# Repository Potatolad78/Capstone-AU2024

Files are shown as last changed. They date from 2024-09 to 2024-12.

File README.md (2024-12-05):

## Table of Contents
1. [Project Overview](#project-overview)
    - [What is pH and how is it important to oceanography?](#what-is-ph-and-how-is-it-important-to-oceanography)
    - [What relevance does this have to computer science?](#what-relevance-does-this-have-to-computer-science)
    - [What use might this project have in high school curriculum?](#what-use-might-this-project-have-in-high-school-curriculum)
2. [Why use this as a project?](#why-use-this-as-a-project)
3. [What will I need?](#what-will-i-need)
    - [Deployment Materials](#deployment-materials)
    - [Perfboard or Breadboard?](#perfboard-or-breadboard)
    - [Wires or Jumpers?](#wires-or-jumpers)
4. [How do I solder?](#how-do-i-solder)
5. [What IDE should I use?](#what-ide-should-i-use)
6. [First Steps](#first-steps)
7. [Soldering Your PerfBoard](#soldering-your-perfboard)
    - [Soldering the Pico](#soldering-the-pico)
    - [Soldering the Power Buses](#soldering-the-power-buses)
    - [Soldering Out Pins](#soldering-out-pins)
8. [Printing Your Parts](#printing-your-parts)
9. [Putting Things Together](#putting-things-together)
    - [Deployment](#deployment)
    - [Connecting Wires](#connecting-wires)
10. [Calibrating the Machine](#calibrating-the-machine)
11. [Troubleshooting](#troubleshooting)
    - [Compartmentalizing](#compartmentalizing)
    - [Taking a Break](#taking-a-break)

## Project Overview
This project, developed by Drew Rigby as a capstone for the Applied Computing major at the University of Washington Bothell, integrates computer science concepts with oceanography, reflecting the intersection of my major and minor. The objective was to design and build an automated pH sensor capable of sampling water and providing accurate pH measurements.

An important goal of this project is to make it accessible for high school students, even those with little to no background in oceanography, coding, or electrical engineering. To achieve this, the project includes a comprehensive manual that provides detailed, step-by-step instructions, ensuring that anyone can build, use, and understand the sensor regardless of prior experience. This focus on accessibility aims to inspire students and foster interest in STEM and environmental science.

### What is pH and how is it important to oceanography?
pH measures the acidity or alkalinity of a substance. This project focuses specifically on the pH of water, a critical parameter in oceanography. One of the most pressing issues in this field is ocean acidification, a phenomenon where the ocean's pH decreases, becoming more acidic.

Ocean acidification has far-reaching consequences for marine ecosystems. For example, reduced levels of calcium carbonate in acidic waters hinder marine organisms, such as mollusks and corals, from forming their shells and skeletons. This disruption cascades through the food chain, potentially impacting human industries and livelihoods. Monitoring pH levels in vulnerable areas can provide valuable insights into the causes and effects of ocean acidification, aiding research and mitigation efforts.

### What relevance does this have to computer science?
This project leverages computer science principles through the use of a Raspberry Pi Pico and embedded systems programming to bring the sensor to life. I applied my expertise to develop a library that simplifies interaction with the sensor, enabling users to perform essential tasks with straightforward functions while maintaining flexibility for advanced customization.

For example, users can easily explore different configurations, such as testing alternative calibration curves using purple instead of green color indicators, by utilizing specific functions provided in the library. This design empowers users to adapt the sensor's functionality to their needs, balancing ease of use with the ability to conduct more complex experiments.

### What Use Might This Project Have in High School Curriculum?
This project is an excellent tool for high school science curriculum, offering students hands-on experience with STEM concepts while encouraging critical thinking and hypothesis testing. The sensor’s flexibility, made possible through its programmable library, allows students to explore a variety of experiments and customize its functionality to suit their needs. For instance, the library includes functions that enable users to adjust calibration curves or test alternative parameters, such as using different color indicators for measurements.

This adaptability provides students with the opportunity to investigate real-world scientific questions, such as how environmental factors like temperature or salinity influence pH levels. By designing and conducting their experiments, students can better understand the scientific method and the role of data in validating hypotheses. The comprehensive manual ensures accessibility, making the sensor usable even by those with little to no prior knowledge of oceanography, coding, or electrical engineering. This combination of flexibility, ease of use, and educational potential makes the project an invaluable resource for inspiring curiosity and fostering skills in STEM fields.

## Why use this as a project?
This project offers a unique blend of accessibility, adaptability, and real-world relevance, making it an excellent choice for educators, students, and STEM enthusiasts alike.

Hands-On Learning: The sensor provides a tangible way to explore STEM concepts, bridging the gap between theory and practice. Students can learn about coding, embedded systems, and environmental science while working on a meaningful, real-world application.

Flexibility: The custom library included with the project allows for significant experimentation and customization. Users can test various calibration methods, explore alternative parameters, and tailor the sensor’s functionality to align with specific learning objectives or experiments.

Accessibility: Designed with ease of use in mind, this project is accessible to individuals with minimal background knowledge in coding, oceanography, or electrical engineering. The detailed manual ensures that even beginners can confidently assemble, program, and operate the sensor.

Real-World Relevance: By focusing on issues like ocean acidification, this project highlights the critical role of technology in addressing environmental challenges. It inspires students to think about how STEM disciplines can be applied to solve pressing global problems.

Incorporating this project into a classroom or individual learning plan can spark curiosity, enhance problem-solving skills, and encourage exploration in the interconnected fields of science and technology.

## What will I need?

|ITEM|QUANTITY|PRICE|
|---|---|---|
|[Raspberry Pi Pico](https://www.adafruit.com/product/5525)|1|$5|
|[Submersible 3V DV Water Pump](https://www.adafruit.com/product/4547)|1|$2.95|
|[Adafruit TSL2561*](https://www.voc-electronics.com/a-37456119/sensors-breakout-kits/adafruit-tsl2561-digital-luminosity-lux-light-sensor-breakout/#description)|1|$7.31|
|[Common Cathode RGB Light](https://www.sparkfun.com/products/105)|1|$2.25|
|[Phenol Red pH Indicator Dye](https://www.poolweb.com/products/taylor-ph-indicator-solution-3-4-oz-dropper-bottle-r-0014-a)|1|$3.38|
|[GT-U7 GPS](https://www.amazon.com/Navigation-Satellite-Compatible-Microcontroller-Geekstory/dp/B07PRGBLX7)|1|$14.99|
|[Cuvette 1.5ML *This link only sells by the 10s*](https://www.amazon.com/Standard-Disposable-Professional-Transparent-Spectrophotometers/dp/B07VGDLMMH/ref=sr_1_3?c=ts&dib=eyJ2IjoiMSJ9.Wdu-PneNgzy9HWgzqQpF4NBLH8vNxU3TnJP97jJI6K5CkgJXkyv-UAtbcqg3fmO8-xdRdEMT4H2ownpaVPMMaHXzsNkF2tbxrW2HuE7zxEcOtA-MBHBYkHV6HmPOE7fLuzGbI9rZSdy10q5kvpcnMFaT6kUqf7-DJbqa2snUjLDDArWAbArXT2QCQDNtBNRAVqzQem_6vUD536fPMKD2lA25uliqrV63WyjNQt6MhQQZa2gJIJN3Nr4TtDbrs_wtAlUK7JVekIs8ODg29hQC5DgXq_pKflS9gyPv6p5u7JI.71dC1E2u98ecs3xq6WpQIMiJ2LN3HRsqwCd--ipGPMc&dib_tag=se&keywords=Lab+Cuvettes&qid=1731213259&s=industrial&sr=1-3&ts_id=318063011)|1|$11.89|
|[20ML Syringe](https://aaprintsupplyco.com/products/neo-sy?variant=32983529488468&currency=USD&utm_medium=product_sync&utm_source=google&utm_content=sag_organic&utm_campaign=sag_organic&srsltid=AfmBOoqIWNiGqBFyY0_SuPJI8O2K_qD1SE5h-Gxxlw2TRUkzQtm_g3tpRyg)|1|$2|
|[Plastic Water Reservoir of your choosing](https://www.berlinpackaging.com/3600b03-2-oz-natural-hdpe-plastic-wide-mouth-packer-bottles-white-screw-top-cap/?utm_source=google&utm_medium=cpc&utm_campaign=PMax%3A%20%28ROI%29%20Shopping%20-%20Smart%20-%20Bottles%20-%20HDPE&utm_id=21016660230&utm_content=&utm_term=&gad_source=1&gclid=CjwKCAjw9cCyBhBzEiwAJTUWNQKtTxFOMuFaX5nl7jv3UimzFBc7M9naBo_MlGrCpJRQH1XFCfGRXBoCqS4QAvD_BwE)|1|$0.38|
|[Peristaltic Pump](https://www.adafruit.com/product/1150)|1|$24.95|
|[Relay](https://www.elecbee.com/en-29076-3V-1-Channl-Relay-Isolated-Drive-Control-Module-High-Level-Driver-Board)|3|$7.99|
|[Tubing](https://www.adafruit.com/product/4545)|2|$1.50|
|[Valve](https://www.amazon.com/SNS-Electric-Solenoid-Normally-Closed/dp/B0D4QN114D)|1|$15.69|
|[Adaptors](https://www.homedepot.com/p/Everbilt-1-4-in-Barb-x-1-4-in-MIP-Brass-Adapter-Fitting-800119/300096726?source=shoppingads&locale=en-US)|2|$4.45|
|Total||$116.62|

\* *They no longer make these sensors but this is all I had access to. In theory any sensor should work you would just need to change the library*
### Deployment Materials
You as the user will have to choose how you would like to deploy the sensor. I have the sensor mounted onto a boogie board with pool noodles attached as that provide flotation for sensor. I will include those materials listed here however
it is important to think of your use case for the sensor and if you will need sturdier materials or if you don't plan to deploy it on water at all instead from a dock.
|ITEM|QUANTITY|PRICE|
|---|---|---|
|[Boogie Board](https://www.dickssportinggoods.com/p/dbx-33-inbodyboard-19dbxudbx33bdybrdsbb/19dbxudbx33bdybrdsbb?sku=25341944&srsltid=AfmBOoplDu2-M7iMlmrVefRNFGweKAaN4pFO5CtZ6sZXx5XDULClXj2LsxM)|1|$14.99|
|[Pool Noodle](https://www.amazon.com/Swimming-Floating-Projects-Exercise-Accessories/dp/B0D5D16BLV?th=1)|2|$0.98|
|[Water Proof Casing](https://www.amazon.com/Waterproof-Plastic-Electronic-Junction-Enclosure/dp/B07M5SZNR9/ref=asc_df_B07M5SZNR9/?tag=hyprod-20&linkCode=df0&hvadid=693308318554&hvpos=&hvnetw=g&hvrand=13402671431230684644&hvpone=&hvptwo=&hvqmt=&hvdev=c&hvdvcmdl=&hvlocint=&hvlocphy=9033316&hvtargid=pla-615797795038&psc=1&mcid=7bd63229ef183828938a82ddd5446444&gad_source=1)|1|$9.49|
|[Cable Gland](https://www.adafruit.com/product/762)|2|$1.95|
|[Ruler](https://www.amazon.com/Mr-Stainless-Centimeters-Drawing-Measuring/dp/B07ZS4JSQP/ref=sxin_17_pa_sp_search_thematic-asin_sspa?content-id=amzn1.sym.04f61faa-8c24-439e-ba3b-8f0078642c9d%3Aamzn1.sym.04f61faa-8c24-439e-ba3b-8f0078642c9d&cv_ct_cx=12+inch+ruler+with+3+holes&keywords=12+inch+ruler+with+3+holes&pd_rd_i=B07ZS4JSQP&pd_rd_r=5daf147d-a691-4b7d-ab83-7f7bf00ba648&pd_rd_w=YHUGZ&pd_rd_wg=niOl4&pf_rd_p=04f61faa-8c24-439e-ba3b-8f0078642c9d&pf_rd_r=GV3FFFXFFZQZWE572363&qid=1733296388&sbo=RZvfv%2F%2FHxDF%2BO5021pAnSA%3D%3D&sr=1-1-baa1f287-65d3-41a3-a655-8bbba0531537-spons&sp_csd=d2lkZ2V0TmFtZT1zcF9zZWFyY2hfdGhlbWF0aWM&psc=1)|1|$5.99|
|[Zip Ties](https://www.amazon.com/Hmrope-Premium-Plastic-Strength-Self-Locking/dp/B07TG9VMWY?source=ps-sl-shoppingads-lpcontext&ref_=fplfs&psc=1&smid=A66IX15EHOXVO)|1|$3.99|
|Total||$39.34|

This does not include perfboards, wires, wiring tools, solder, soldering tools, or resistors. Those can be found below if you do not have them otherwise please skip past to the [Soldering Your Perfboard](#soldering-your-perfboard) section
This also does not include adhesive, I would recommend getting yourself some kind of strong sealant for creating the seal around the bottom of the cuvette and the valve however you could in theory use hot glue if you're good enough with it.
### Perfboard or Breadboard?
Perfboards are used when you are creating electrical circuits and would like a stable connection that doesn't require having jumper cables. This
does require soldering for connection of pins which can be dangerous if unsupervised. This also allows for less errors as things are easier to 
break. If you are going with perfboards I recommend a breadboard layout as there are the easiest to use as they have power buses(See Vocabulary)
built in. If you are going to use perfboards I would recommend using a bread board to make sure that you have a good understanding of the 
electronics before soldering things into place.


You can find a good perfboard [here](https://www.adafruit.com/product/1609) for $4.50

Breadboards on the other hand are less permanent but can have issues with pins not touching metal properly and are often seen as temporary solutions.
As said above in the perfboard section one should at least use a breadboard to plan out their circuit so one could save money by only using breadboards.


You can find a good breadboard [here](https://www.mouser.com/ProductDetail/SparkFun/PRT-12002?qs=WyAARYrbSnYNJEbsmDuXsA%3D%3D&mgh=1&srsltid=AfmBOopsiO3PD5JWbhyFv99flrAnsKZhypC7DzSwbdvFXANliHVx4DNLneM) for $4.95

### Wires or Jumpers?
Choosing between buying wires or jumpers is very difficult. If possible one should buy both as it allows for modularity when creating the ciruits however
if you can only afford one option then there are many things to consider.

#### What tools do I have acccess too?
If you have access to no tools and are trying to do this project without using any you are going to have a difficult time. If you are still going to try to
replicate the project without tools then you are going to want to go with jumpers as you wont have to wory as much about shortening them to the size that 
you need. However you will have to at least have access to solder for this project as not every module on the project has headers and to use jumpers you will
need to solder on headers. If you have access to things like wire cutters and wire strippers then normal wire should work perfectly. This will allow you to 
have more modularity and wires also just feel more professional. It also helps if you have solder sleeves and a heat gun as it allows for less precision when
soldering as for difficult things you can use said solder sleeves instead.

### How do I solder?
Soldering is a skill in its own right that is very difficult to master. For this project you should allocate a week or more to making sure that your skills 
are properly up to par with solder before permanently setting things into place. I recommend starting with watching this video:
<a href="http://www.youtube.com/watch?feature=player_embedded&v=rK38rpUy568
" target="_blank">IMAGE ALT TEXT HERE</a>

### What IDE should I use?
Before we get there it is important that you install the proper packages for python and install python itself. Installing python can be done [here](https://www.python.org/downloads/)

When python is done installing then you should also be able to run these commands in your terminalto get the needed libraries installed.

```console
pip install pyserial pandas matplotlib
```

You should install [Thonny](https://thonny.org/) as it will detect when you connect your pico to the system and on the bottom left you should be able to click
the com that your pico connects to and be able to edit code on said pico. To test this you should install the library directory and the main.py from the repo
onto the pico. Do this by going into Thonny, detecting your device and making sure that you have the device open it should look like this:



Highlight the files that you would like to move into the pico and then right click under the rapsbery pi pico section. It should say intall to and then have a directory
or an empty signature. Do that and see if those files are now in the pico section, if they are you succeeded in downloading those files onto your pico. Try also
creating a file on the pico, right click under the raspberry pi pico section and then click create file. Name said file test.py, this should open the file on 
the IDE. Go ahead and write:

```python
print("Hello World")
```

Then click crtl s and save the file. You should see the file appear on the bottom left side of your screen as test.py. You can now run your file using the green check mark in
the top left. Keep this file as when I have code written you can use this file to copy and paste said code into to make sure your components are working correctly

## First Steps
Going forward I am going to assume that you are going to be working with proper tools, wire, perfboards, and will be soldering. I am also going to assume that
you 3D printed the parts that are required in the project. If you do not then you will have to go off from the instructions. If you have questions you can email
me at the email phsensorguide@gmail.com.

## Soldering Your PerfBoard
### Soldering The Pico
When soldering your perfboard it is very important to try and avoid errors as these sre semi permanent. 
Raspberry Pi Pico Pinout
[Link to Pinout](https://microcontrollerslab.com/raspberry-pi-pico-pinout-features-programming-peripherals/)
I personally recommend that you dtart by soldering female header pins into the perfboard. The pico is 20 pins long so you will need a long enough strip of pins.
If you have a strip that us longer then you can use wire cutters to cut it down to size. Try and solder in a diagonal pattern, soldering one corner then another.
Remember that you should also be soldering the UNDERSIDE of the board and not the top. This along with a stabilization method(Tape the item into place in the front side) 
should help keep the female headers straight so you can slot the pico in flush.
The following picture is an example of pins soldered onto a board:
Pins on Perf
The following picture is an example of a pico slotted into header pins. (Note your female pins should be soldered onto the board not the pico)
Flush Pico

Once you have completed that you have successfully done the first step, congratulations! Next we will solder the power busses.

### Soldering The Power Buses
You should have space for two power busses on your perfboard. Assuming that you bought the perfboard I recommend then the two strips on the side are dedicated busses.
If you did not buy that board then you will have to solder your connections(Please note I will not be covering bridging connections and I recommend watching a video 
on it). You will see on your perfboard that there is a red positive side for the bus and a blue negative side. This means you will need to solder the battery ground
to the blue side and the power to the red side. Remember one bus is 3 volts and the other is 12 volts so you should have a 3 volt battery pack and a 12 volt battery
pack. 

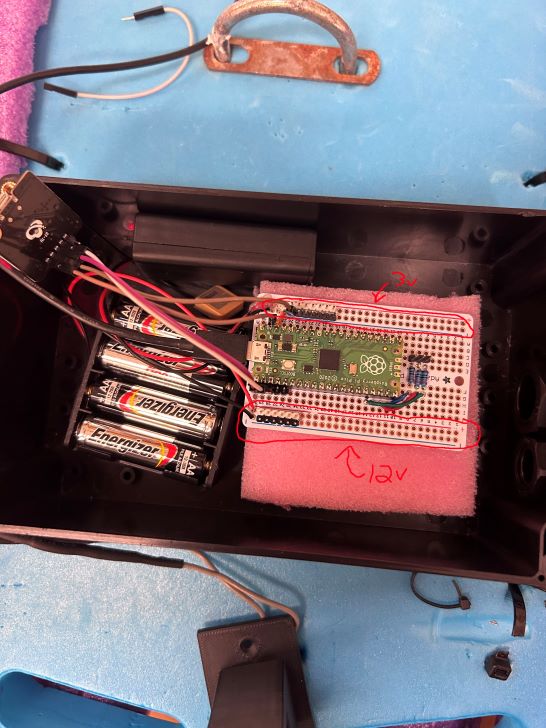
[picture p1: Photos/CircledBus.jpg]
PowerBus


If you have a multi meter you can test your work by powering the battery and putting one side to positive and another to ground on the board and then switch to voltage.
Some wires that come out of battery packs are flimsy so you should try and use an adhesive to keep them in place, I used super glue. If you did this correctly you will see the 
correct voltage read on the multi meter. If the voltage seems slightly off then check to see if your AA batteries are fully charged. Next we are going to solder male headers 
onto the busses so we can connect jumpers. You will need at least 7 available headers on both power and ground for 3 Volts and at least 4 for both positive and ground for 12 volts. 
Since we have gone over the process already I wont here but follow the same principles and all should go well. 

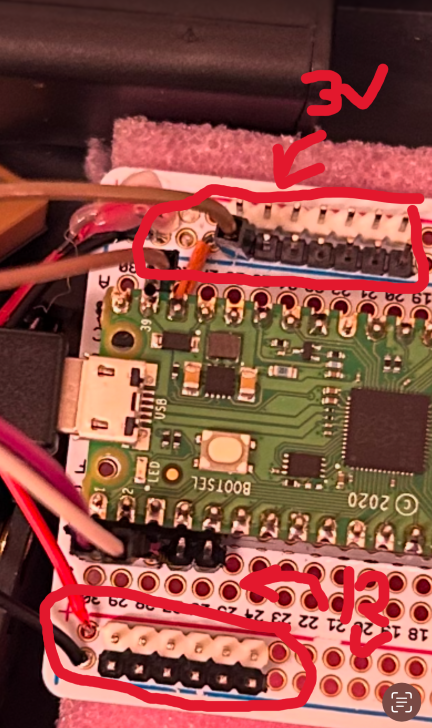
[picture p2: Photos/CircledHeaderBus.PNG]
HeaderCircle


Once your busses are done we only have a few more headers to solder!

### Soldering Out Pins
By now you should have some experience soldering so I will be using less detail so please refer to previous sections for questions or contact me. 
Now we will connect the pico to the 3V ground with a wire(if you only have jumpers you will need to cut the ends off of it and strip it to be used as a wire.) Using the Pinout 
diagram locate the ground closest to the USB2 port and the 3V Bus. 
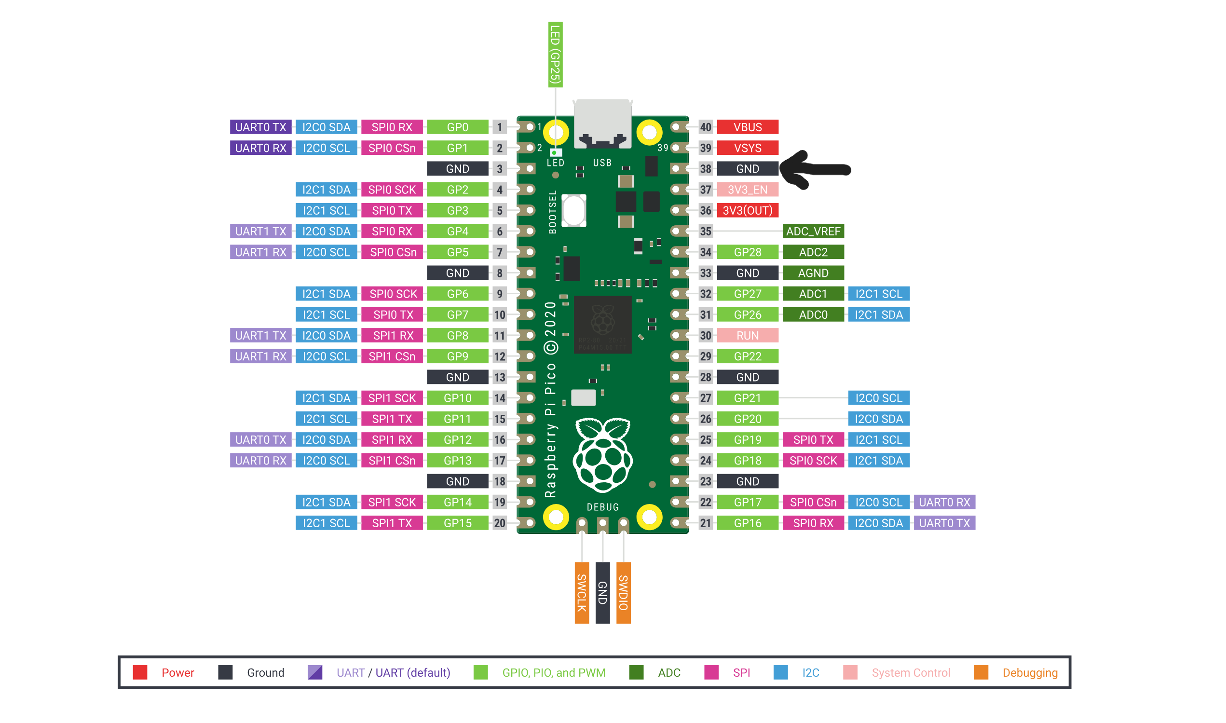
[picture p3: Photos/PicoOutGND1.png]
Correct Pinout

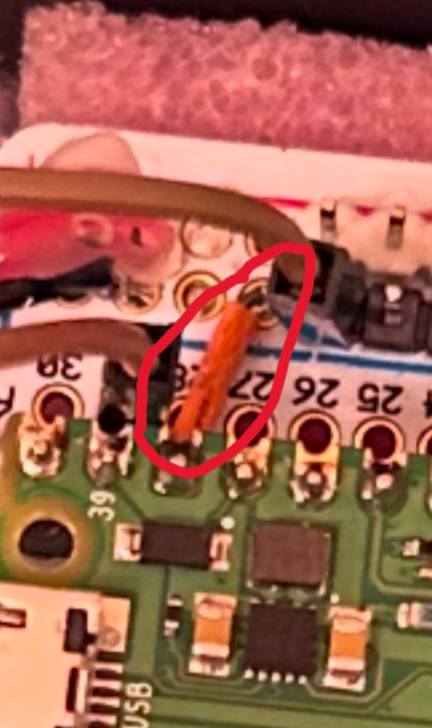
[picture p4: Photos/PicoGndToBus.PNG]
Example of Wire


Now we will be soldering one end of the wire directly next to the ground of the pico that is highlighted above and the other end to the ground bus of the 3V battery pack. 

Right next to that ground is the VSYS pin, this gives 5 volts of power which will be used for the GPS. We will solder a male header right next to that VSYS pin so you can 
use a jumper to connect to the GPS and power it.

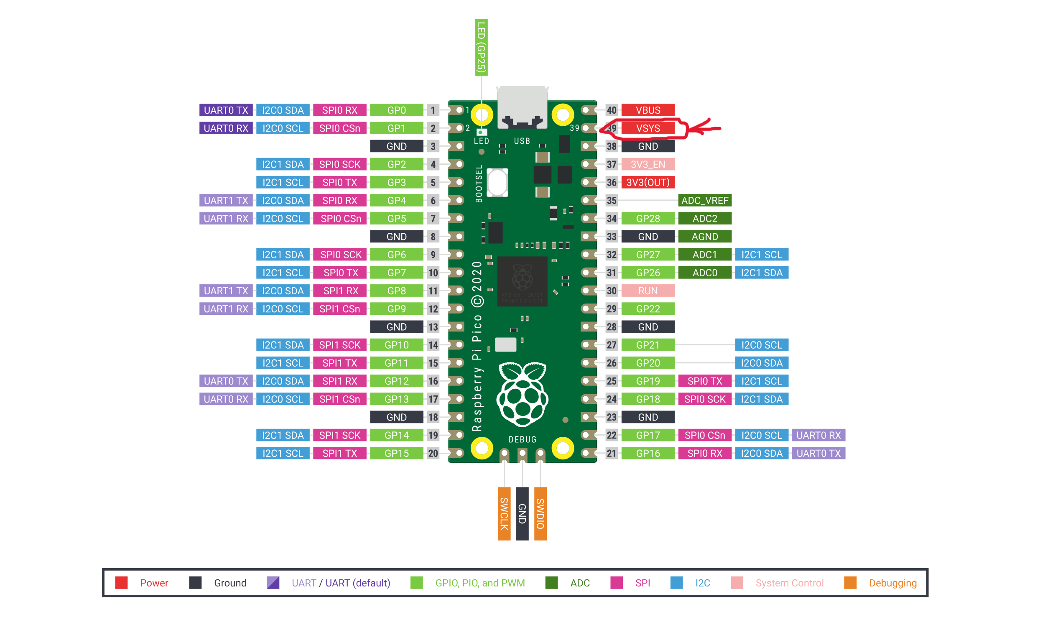
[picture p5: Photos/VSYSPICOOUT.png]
PicoOut

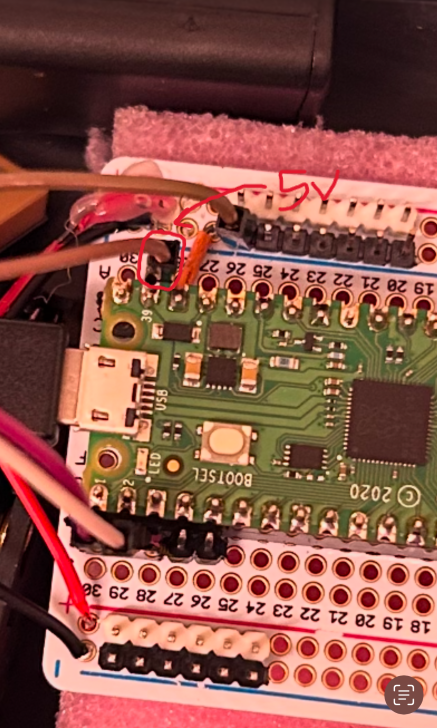
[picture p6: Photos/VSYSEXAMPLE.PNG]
Example of VSYS


Next we will be soldering male header pins next to GPins 0,1,2,3,18,19,and 20. It will be the same as previous male header pins.

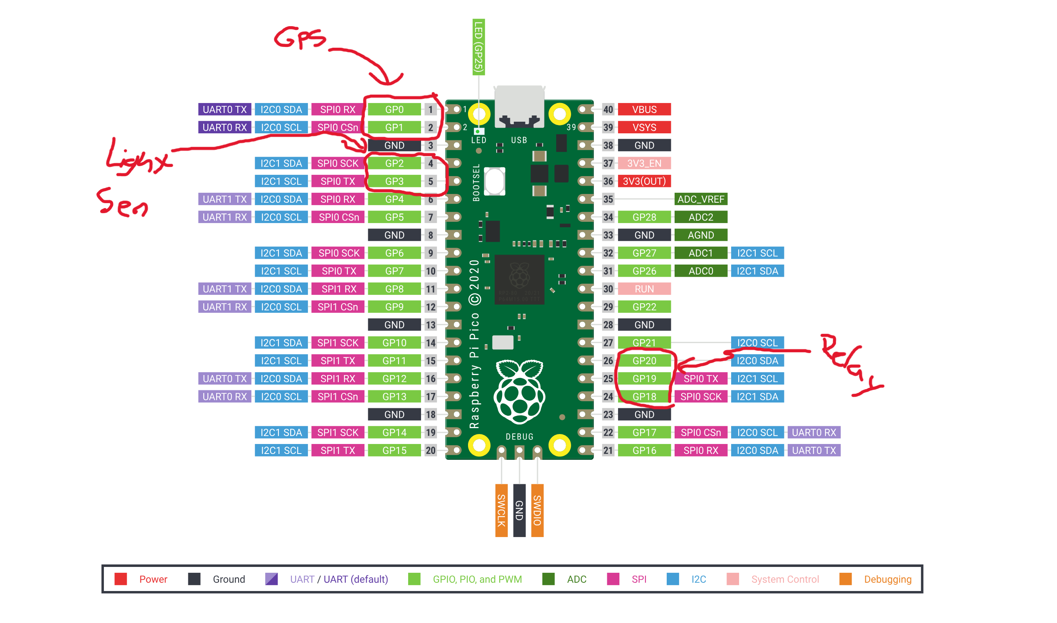
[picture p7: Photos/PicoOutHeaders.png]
PicoOutHeaders

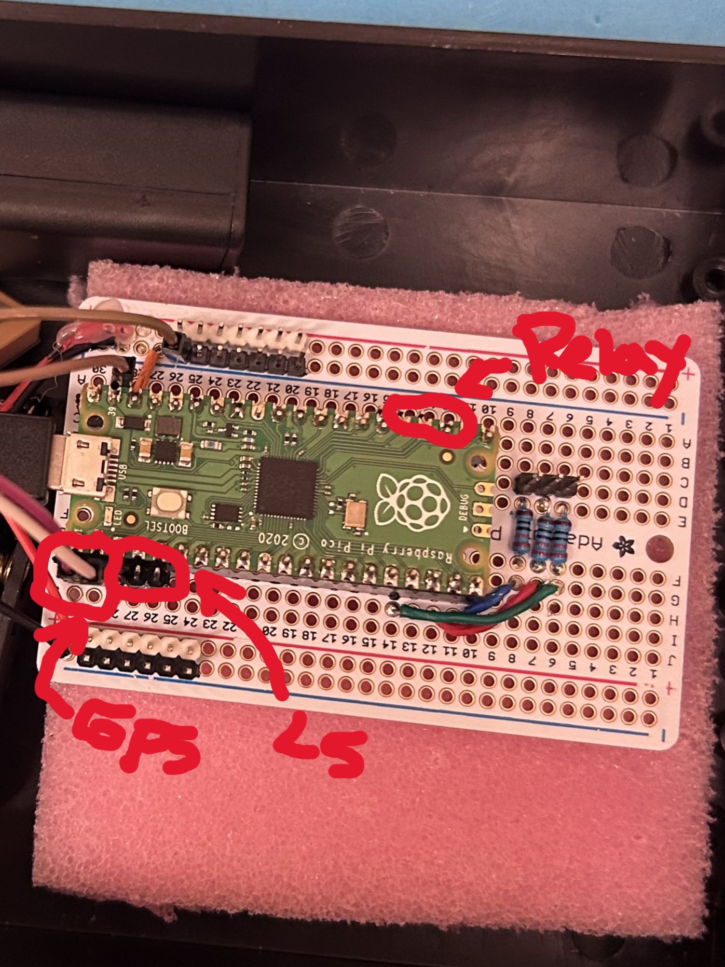
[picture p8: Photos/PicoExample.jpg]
PhotoOfPico


Finally we are going to solder the headers and cables for the RGB Light. This is were we will use our 220ohm resistors. As seen in that image:

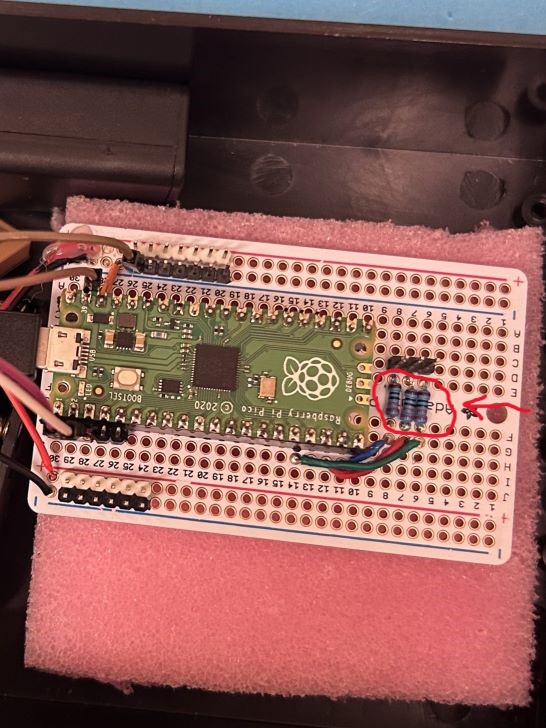
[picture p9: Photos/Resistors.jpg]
Resistors


Using the same wiring process as before we are going to solder wires from GP 13,14,and 15 to the BOARD rows 8,7,and 6. It is important that you are not wiring to pins on the pico
instead you are wiring to empty rows on the board. You should leave one empty slot between the cable and the middle gap as that is where the resistors are going. I recommend wiring
GP 13 to board row 9, GP 14 to row 8,and GP 15 to row 9. You can also color code your wires to help you remember what pins reflect what colors on the led. Once you do that we are
going to solder in the resistors. The resistors should bridge the middle gap on the board and connect to the corresponding side. Think of it as part of the wire so you want it to be inline
with the same rows. Once your resistors are done you can now solder male headers on the side of the board with no wires as in the photo:

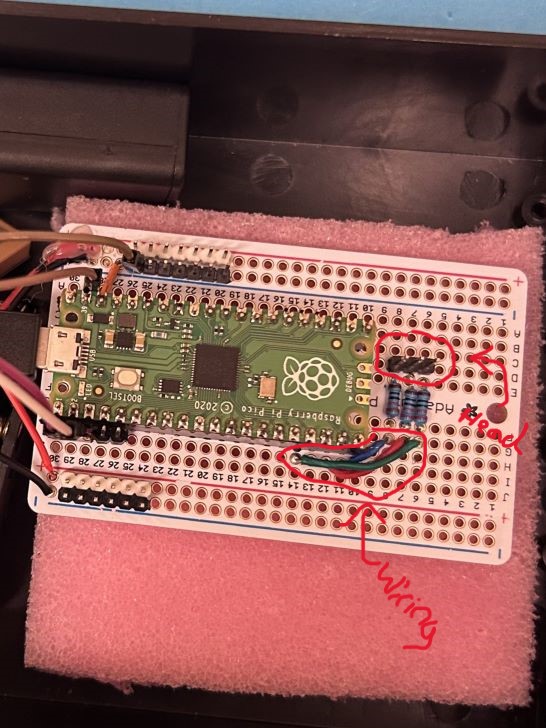
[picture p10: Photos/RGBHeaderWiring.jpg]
RGBHeaders


Once those headers are soldered you are all done with the perf board! Congratulations!

### Soldering GPS and Light Sensor
Depending on your setup this could be your last bit of soldering! You simply must solder some male headers onto your light sensor and GPS so you can connect jumpers to them. This is just
the same as soldering the board except you must be a bit more delicate as overflowing solder is more likely to cause issues. 

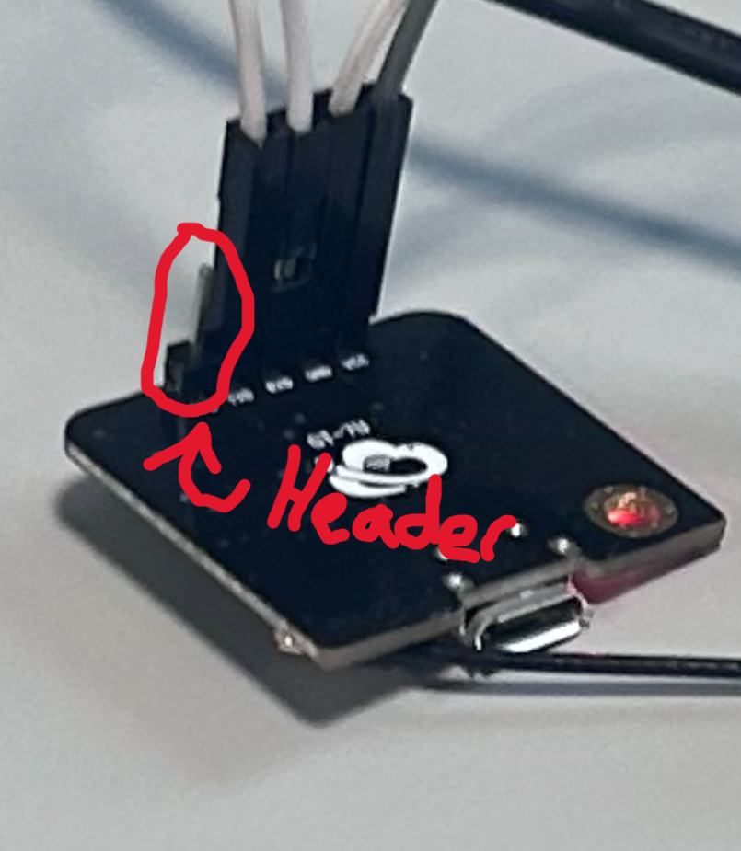
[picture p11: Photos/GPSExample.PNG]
GPSExample


If you have a heat gun and solder seal wire you are done soldering! If not there will still be some soldering. Going forward I will be assuming you have a heat gun and solder wrap however
solder wrap only does the job of soldering and covering exposed wire so you can do that with solder and heat shrink or electrical tape. 

## Printing Your Parts
Now that you have got your soldering done its time to go about 3D printing the required parts in the CAD folder of the repo. All designing is already done for you so you can take
those files to a 3D printer, enter them, and begin the printing while we connect all of the wiring together. If you don't have a 3D printer check your local library and if they don't
have one available check your school.

## Putting Things together
### Deployment
While your parts are printing we are going to get back to putting things together. The first thing that you will need to do is set up your deployment method. The following photo is a
picture guide of what we will be doing:

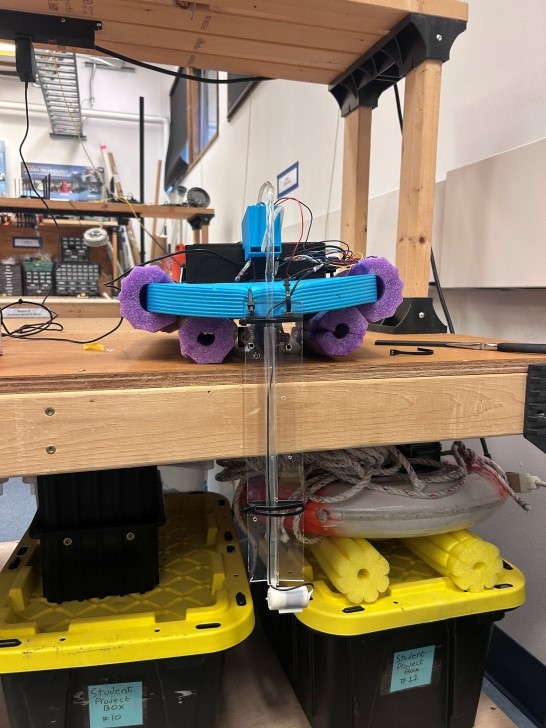
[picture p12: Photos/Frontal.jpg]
Frontal Image


Start by cutting the pool noodles in half length wise. Take two halves of the pool noodles and cut enough of a section out they can comfortably wrap around the edges of the boogie board.
Poke three holes in the boogie board on each side near the pool noodles. Through each hole run zip ties through and around the pool noodles to strap them into place. Finally attach the
final two halves of pool noodle under the boogie board and strap them to the boogie board using the same zip tie method.

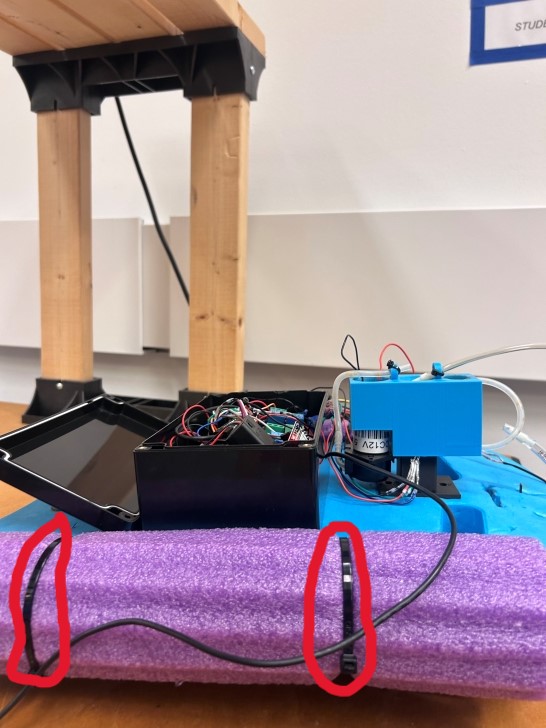
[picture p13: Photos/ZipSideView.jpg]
Ziptie


Now we are going to drill holes in the side of our box to run cables out. They should just be big enough to fit a cable gland through, once it is through you should tighten the nut on the
inside and using the rubber seal. Attached will be a video link that shows how to do so [here](https://www.facebook.com/waterproofcablegland/videos/how-to-install-the-cable-gland-to-the-junction-box/700374587211266/)

Once that is done your box should look something like this:

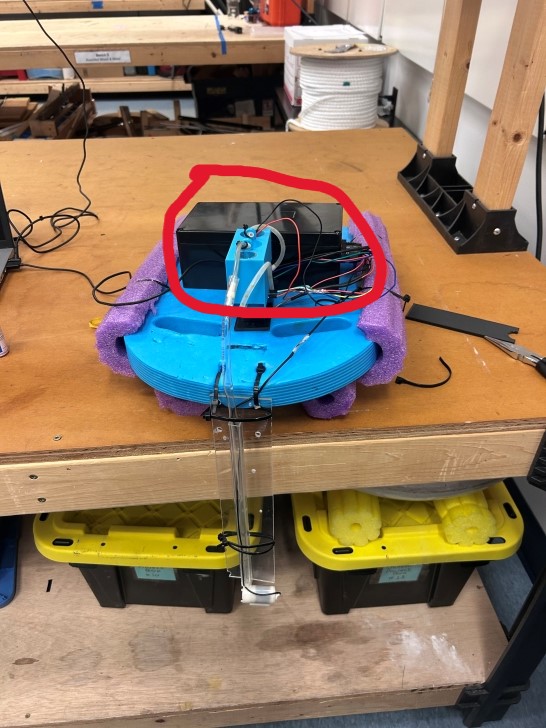
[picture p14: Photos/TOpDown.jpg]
Topdown


Now you have to run a zip tie through the top of the ruler and secure it to the front of your boogie board using the same method used with the pool noodles. Poke a hole in the front of the 
board and run a zip tie through it and the ruler and lock it straight down. You will then need to secure you DV pump to the bottom of the ruler as seen here:

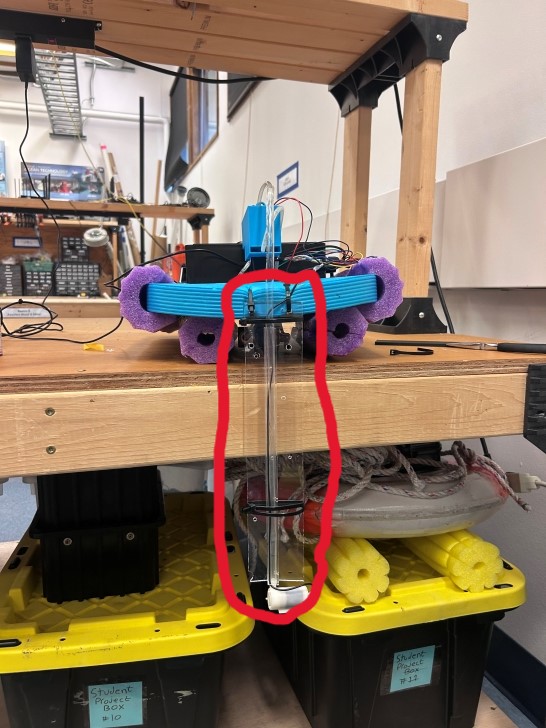
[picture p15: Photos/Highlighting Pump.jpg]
HighlightingPump


You will also have to run tubing to the pump so it is important to make sure that it isn't flailing around. Zip ties can do the job just remember not to cut off any flow of the pump as it is 
very delicately measured in terms of timing and anything could change said timing. Once the tubing to the pump runs all the way up you want to make sure that you cut it to size. That is where 
the printed parts come in. You should now have your parts hopefully and can install them. The first thing to be installed will be the cuvette holder. This can be installed by drilling a hole 
through the bottom of it and through the boogie board about the size of the tubing that you have. Once that is done you will have to create the cuvettes. When creating the cuvettes it is 
important that you slowly up the drill bit size as just going to the size of the tubing will cause the cuvette to crack which will lead to leaks. I would drill out a few cuvettes if you got
the bulk shipment as they tend to be somewhat flimsy. Once done with that you should then use your adhesive of choice to secure the tubing to the bottom of the cuvettes. It should only be about 
6 inches of tubing max for the cuvettes each as all it is doing is connecting the cuvette to the valve. While doing that cut out a few inches of tubing to connect your valve to your container.

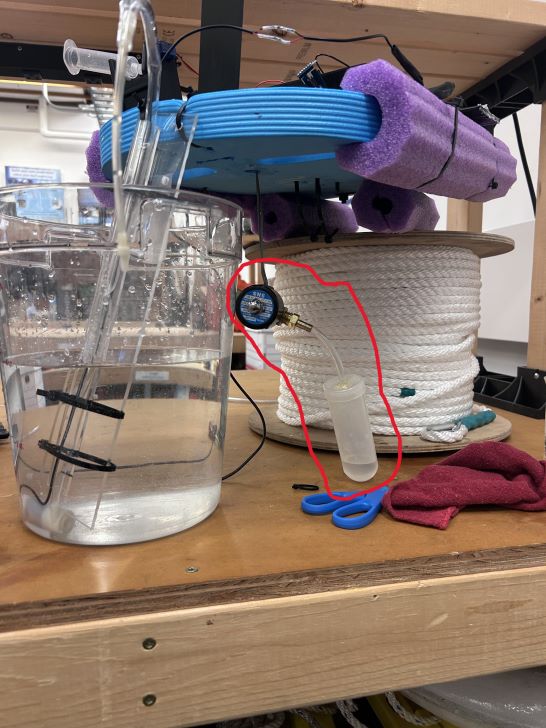
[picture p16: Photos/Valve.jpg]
Valve


That tubing can be applied to one end of the valve and then run to the plastic waste container which then have to have a subsequent hole cut through it and adhesive will have to join the tubing
with said container. Now your cuvettes should be dry, make sure to test that they aren't leaking as if they are it can cause damage to the electronics and will make it almost impossible to get a
sample. Run the cuvette tubing through the whole that goes through the cuvette holder and the boggie board. It should reach down to the valve under the boogie board which can then be connected.
You can also run the valve wires through the same hole upto the box.

Once you make it to the cuvette cover you should make sure to place around an inch of tubing at the bottom of the syphon so that the water is all directed into the cuvette.Then you will need to 
put the peristaltic pump into the cuvette cover. It is a very snug fit so don't be afraid to really push it in there. If it is to tight to push in you can use a file and get rid of some of the 
material. On the other side take out the syringe plunger, remove the tip from the syringe and place the whole syringe into the side of the cuvette cover that doesn't have the pump in it. You 
can then cut the syringe down to size and make sure that it sits flush with the cuvette cover while also leaving room for the intake tubing from the peristaltic pump  to fit through the gap 
on the bottom of the cuvette cover.Then run the tubing out from the peristaltic pump  It should look something like this:

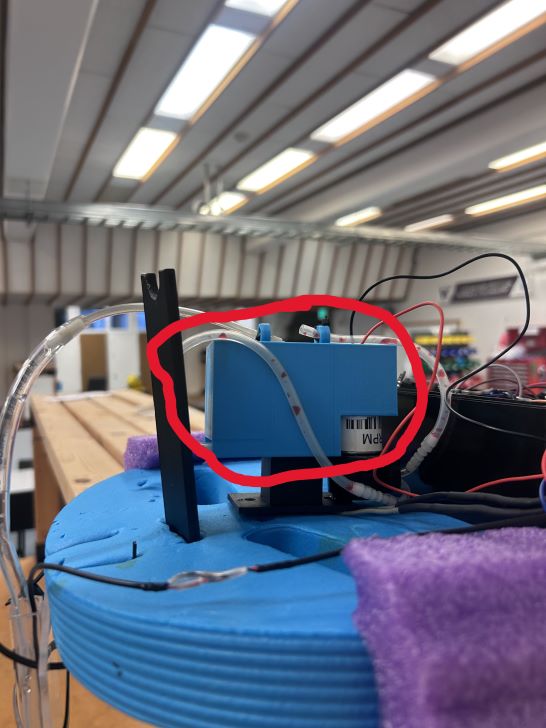
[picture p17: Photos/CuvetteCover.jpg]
CuvetteCover


Now you just have to secure the box to the boogie board. I used super glue but you can use whatever you would like to secure the box to the board but once you are done we have our deployment
method finished. It should look something like this without the wires everywhere

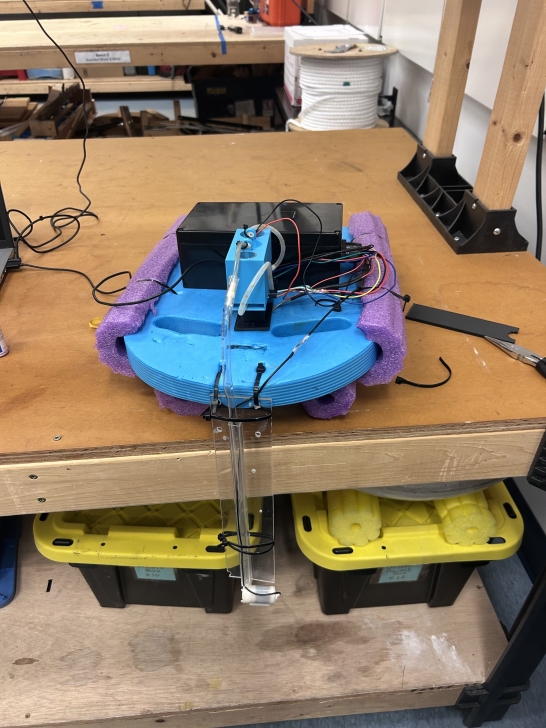
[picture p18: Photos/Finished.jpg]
Finished


### Connecting Wires
When trying to connect jumpers with longer wires you will likely want to use solder wrap. If you don't have it you will just have to cut wires and solder them together and then cover with either 
normal heat shrink wrap or electrical tape. But if you do have the wraps then you can watch this video on how to join wires with them:

<a href="http://www.youtube.com/watch?feature=player_embedded&v=lmfiOJjRwRk
" target="_blank">IMAGE ALT TEXT HERE</a>

Just remember this is created using jumpers so I am expecting that you will be connecting wires together with jumpers to extend the total distance needed.

Now we just need to wire things up and we will be on our way to take samples. The first thing that we will wire will be our GPS. Connect TX to GP0 and RX to GP1, followed by the VCC to the
VSYS header along with the ground to the 3V ground bus as that is grounded to the pico. If you did this successfully you will find that when you connect to your pico your GPS will have a red
LED on. Next we will connect our light sensor. Run the VCC to the 3V Bus positive and the ground to the 3V ground. Run the SDA cable to GP2 and the SCL to GP3. You can test to see if this worked
by running the following code in Thonny on a raspberry picco

```python
from machine import Pin, I2C
import tsl2561
i2c= I2C(1, scl = Pin(3), sda = Pin(2))
sensor = tsl2561.TSL2561(i2c)
print(sensor.read())
```

If the code does not provide an error and instead prints a number you were successful. You can then slot this into the cuvette holder in the slide.

Next we will connect out RGB light, first you should test to see what pin corresponds to what color for the light. Using a multi meter put the ground on the longest pin and the positive on any other
pin. Make sure the multi meter is on the sideways wifi symbol and this should cause the light to go off with the corresponding color. Do this with each other pin and you will now know what pin 
corresponds to what color. Connect the pin that corresponds to red on the light to row 9 on the board green to row 8 on the board and finally blue to row 7 on the board. If you were successful
you should be able to run the following code in your test file by deleting the current contents and pasting the following:

```python
from machine import Pin
from time import sleep

red = Pin(13, Pin.OUT)
green = Pin(14, Pin.OUT)
blue = Pin(15, Pin.OUT)

red.value(1)
sleep(2)
red.value(0)
blue.value(1)
sleep(2)
blue.value(0)
green.value(1)
sleep(2)
green.value(0)
```

If this causes your light to flash red then blue the green over 2 second intervals then you successfully worked the pins. If the colors do not go in that order you may have wired things differently so
you should move the corresponding wires to places that lead them to flash in the correct order. If there is no flashing that means the soldering was not complete and I would either reach out to me 
or reach out to an experienced solderer for help. If all works you can slot this into the small hole on the side of the cuvette holder.

Next we are going to connect the final three pins. Each pin will be run into a relay that will control either one of the pumps or the valve. Make sure that VCC and Ground are run to the 3V bus for 
power.With relays you must unscrew the top, feed the wire in, then screw the top back down to hold the wire in place and to also make sure that there is a connection where there should be. That 
goes for all three of the relays as they all require the same power. For the in section run 18,19,and 20 into them, this should be done with a male to female jumper. Run power from the 3V bus to 
the COM side of the relay that you plugged GP19 into. For GP18 and GP20 relays they should have power coming from the 12V bus into the COM section. Plug The ground from the peristaltic pump and the
valve into the ground for the 12V bus. Plug the DV pump ground into the 3V bus ground. Now plug the DV Pump power into the NO section of the GP19 relay. Connect the peristaltic pump power into the 
GP18 Relay NO section and finally the valve power into the GP20 NO section. If done correctly you should be able to run this code

```python
from machine import Pin
from time import sleep

dyepump = Pin(18, Pin.OUT)
waterpump = Pin(19, Pin.OUT)
valve = Pin(20, Pin.OUT)

dyepump.value(1)
sleep(2)
dyepump.value(0)
waterpump.value(1)
sleep(2)
waterpump.value(0)
valve.value(1)
sleep(2)
valve.value(0)
```

This should run the dye pump for two seconds, the waterpump for two seconds, and you should hear the valve open for two seconds then close. If the order is incorrect then the relays were wired incorrectly.
That is all of the wiring congratulations you are almost done!

## Calibrating the Machine
When calibrating your machine it is best to have the most samples that you can. You want water that is ranging from 5pH to 10pH to create a better curve. The more data you give the machine the more accurate
it will be. I achieved +-0.2 pH with my calibration curve using only data from 5, 7, and 9 pH so with more im sure that the results would be much better. There will be some input that you will have to do however.

The first thing that you will need to do is go to pH_sensor_lib.py and go to line 226

```python
averages.append(average/207.0545)
total_average += (average/207.0545)
```
You will need to remove the 207.0545. If everything up to this point has been working then you should be able to run pc_side_collection.py. Disconnect your pi and reconnect it. It should flash a blue light first and 
then you will be able to run the file. Once it is finished you will get back a csv with data in it. That means everything is working properly. Fill your cuvette with clear water and repeat the same process starting 
from you removing the usb and reconnecting it. The reading should come through and that will be your default data that will take the place of 207.0545

```python
averages.append(average/#Your data here)
total_average += (average/#Your data here)
```

Now you can run tests with your known samples. Repeat the same process except instead of clear water get the water solution that you know the pH of in a range of 5 - 9 pH. Drop two drops of phenol read in the cuvette and 
shake it with it covered. Take your sample and now you will use these results to create your curve. You should get a decimal number something like what you would find in pc_side_collection.py line 45
``` python
'x': [5, 7, 9],  # Known x-values (pH values)
'y': [0.982363, 0.434377, 0.127482]  # Corresponding y-values
```

Change the x to your known pH and the y to the corresponding value that you got. The data in there is from my calibration curve if you would like to use it you can but it will not be as accurate as your sensor will have 
small differences from mine. However once you fill this out you should start to see a graph that is being made from these data points. Once you are happy with the curve then you should be able to do the same with data that 
you have not plotted that are somewhere within the values that you have. For example if you plotted 6.5 and 7 you would be able to test water if any pH between them and have the correct pH spit out. Here is where you can
check your curve and see if it is as good as mine or if it is even better!

Once you are done creating your curve you can make sure that your timing for the machine is correct.

**IMPORTANT:** When testing the machine with actual water and dye flowing through the pumps it is important to move the light sensor and light away from their slots in the cuvette holder.

Making sure that the tubes are fed through the cuvette holder as shown here:

INSERT PICTURE OF STUFF THROUGH THE HOLDER

You are ready to go. Go to ph_sensor_lib.py and go to line 181

``` python
        self.dPump.value(1)
        self.wPump.value(1)
        sleep(3.1)
        self.dPump.value(0)
        self.wPump.value(0)
```

This is the timing that the pumps turn on and off. You will need to make sure that this fills your cuvette as to a safe level and that enough dye comes out. To change the time that the pumps are on you change the number in the sleep
function. For example the pumps that I ran needed to be on for 3.1 seconds exactly to get the result that I wanted. However if I wanted them to run for 1 second I would do

``` python
        self.dPump.value(1)
        self.wPump.value(1)
        sleep(1)
        self.dPump.value(0)
        self.wPump.value(0)
```

You can also have certain pumps run for certain amounts of time, dPump refers to dye pump and wPump refers to water pump. For example if I wanted the dye pump to run for 1 second but I wanted the water pump to run for two I would do
``` python
        self.dPump.value(1)
        self.wPump.value(1)
        sleep(1)
        self.dPump.value(0)
        sleep(1)
        self.wPump.value(0)
```

Just remember that when you want to test you would just run pc_side_collection.py Here the water pump waits for an extra second after the dye pump turns off and continues pumping and then turns off. Continue messing with this until you 
find the timing that works for you. Remember though you do not want to overflow with electronics slotted as you will fry them. Once you have your timing down you can get your first automatic sample! just run pc_side_collection.py and 
you will get your first sample congratulations and thank you so much for trying my project!!! Please contact me with your successes as I would be delighted to see them.

## Troubleshooting
Since I wont be there directly with you I wont be able to help you trouble shoot on the fly however I will be able to troubleshoot over email as stated above. I will also share some methods that have always helped me.

### Compartmentalizing 
When trying to locate a problem with the technology it is important to try and remove as many variables as possible and try to find the root cause of the issue. That may mean that you think it is the code so you run bit by bit. This is 
designed to be very lightweight coding for people but if issues arise it is a great way to try and build some debugging skills. The more likely issue however is hardware not matching with software, things not being plugged into the spots
I marked for you to put them into or their connection being poor. Always read the error messages try and get smaller and smaller ones till you find the issue.

### Taking a break
It is important to remember that this was designed over a long period of time and that it will not come without any issues. Taking breathers is crucial to success.

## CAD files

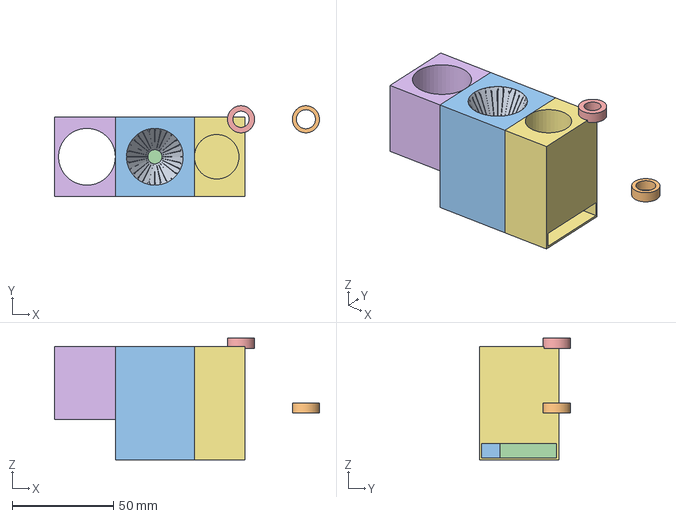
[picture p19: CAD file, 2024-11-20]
CADFiles/WIP-DrewRigby2.3mf
130.7 x 44.7 x 60.0 mm

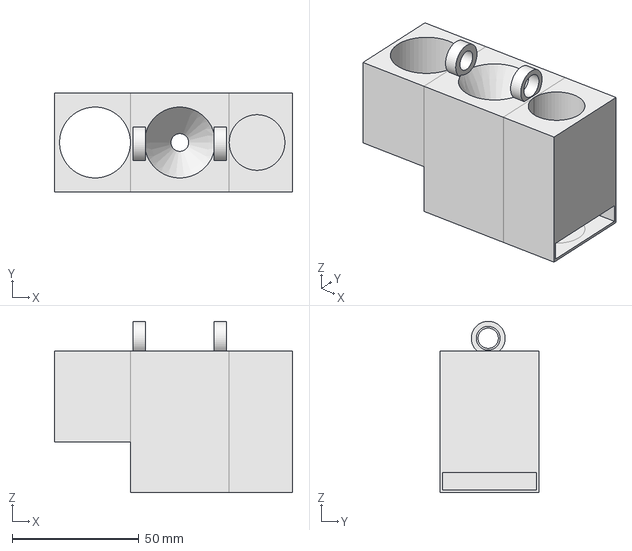
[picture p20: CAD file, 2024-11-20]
CADFiles/WIP.FCStd
94.0 x 39.0 x 67.7 mm

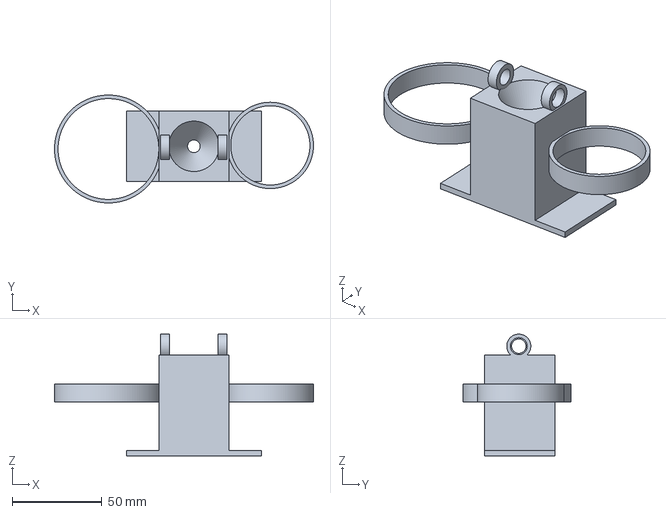
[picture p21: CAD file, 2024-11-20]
CADFiles/WIP-DrewRigby.3mf
144.0 x 60.0 x 67.7 mm

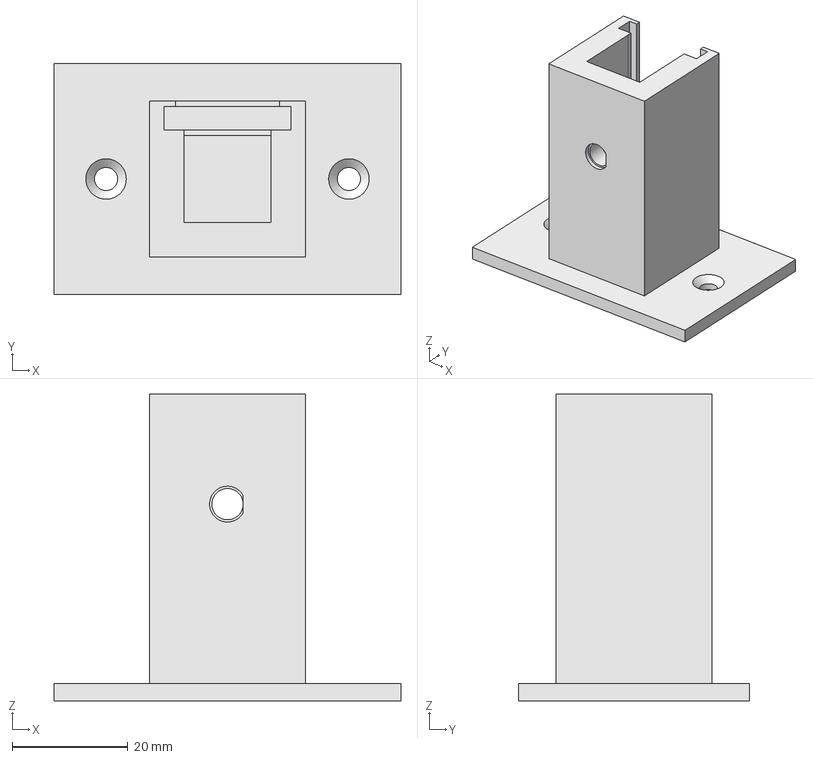
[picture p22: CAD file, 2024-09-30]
CADFiles/light_chamber_final-Cuvette Holder.step
60.0 x 40.0 x 53.0 mm

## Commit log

2024-11-10 Added pump
2024-11-12 Testing from pi
    [pH_data.csv]
2024-11-20 Redid Library
    Added Library and also began looking into the possibility of having the data instantly plotted via py using serial communcation
    [WIP-DrewRigby.3mf, WIP-DrewRigby2.3mf, WIP.FCStd]
2024-11-26 Functional Implementation of Last Push
    [data.csv, results.csv]
2024-11-26 Updated lots but it all works now
    Added full automation
    [data.csv]
2024-11-29 Added GPS
    [data_1.csv, data_2.csv, data_3.csv]
2024-12-04 Backed up Unneeded Files
    [data_1.csv, data_2.csv, data_3.csv, pH_data.csv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]
